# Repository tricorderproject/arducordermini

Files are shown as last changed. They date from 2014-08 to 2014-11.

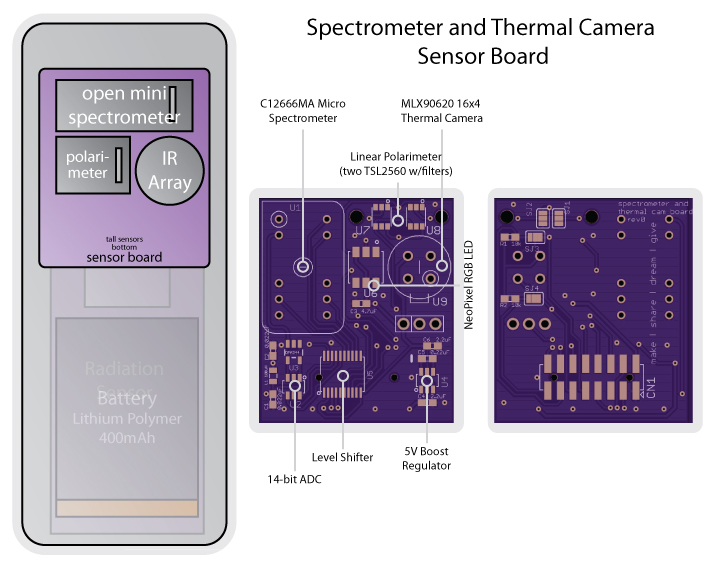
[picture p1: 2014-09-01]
hardware/pictures/spectrometer_rev0_layout.jpg

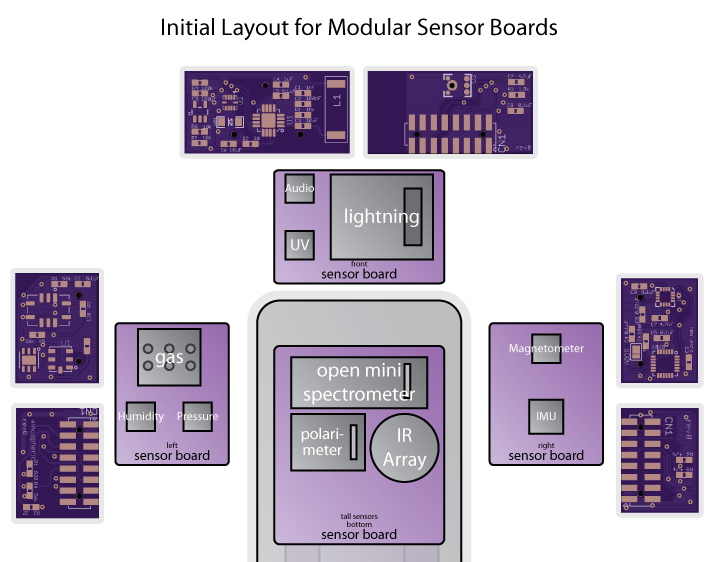
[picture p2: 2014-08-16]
hardware/pictures/sensorboards_rev0_layout.jpg

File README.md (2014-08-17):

Arducorder Mini
======

Arducorder Mini -- an Arduino-compatible Open Source Science Tricorder Project  
http://www.tricorderproject.org  
Copyright (C) 2014  Peter Jansen and the Tricorder project  
peter@tricorderproject.org  

*This is a work in progress*

# Introduction

This is the third iteration of the Open Source Science Tricorder prototypes, a series of science tricorder-like devices.  

Unlike the first two prototypes, this version has been designed from the ground up to be easy to manufacture, and to foster a community of open source developers and users.  The firmware is Arduino-compatible through the ChipKit MAX32 platform, and is being designed to provide advanced functionality for scientific use while being easy enough for beginners to meaningfully modify. 

# Concept
It is my deep belief that knowledge brings about positive change. 

We could live in a world where the same instrument that can show a child how much chlorophyll is in a leaf could also show how them much pollution is in the air around us, or given off by one's car. As an educator and a researcher, I feel that if people could easily discover things about their worlds that were also important social topics, that they would then make positive social choices, like reducing their emissions, or petitioning for cleaner industry in their communities. 

By having access to general inexpensive sensing tools, people can learn about healthy leaves, clean air, clouds and the water cycle, energy efficient homes — and visualize abstract concepts like spectra or magnetism. 

As a tool for exploration, we can discover things around us that we don't already know. And that's what it's about. Little discoveries, everywhere.

# Open Source

This project is open hardware and is released under various open licenses.  Please see LICENSES.TXT for details.

# Warning

**DISCLAIMER OF WARRANTIES AND LIMITATION OF LIABILITY.**

UNLESS OTHERWISE SEPARATELY UNDERTAKEN BY THE LICENSOR, TO THE EXTENT POSSIBLE, THE LICENSOR OFFERS THE LICENSED MATERIAL AS-IS AND AS-AVAILABLE, AND MAKES NO REPRESENTATIONS OR WARRANTIES OF ANY KIND CONCERNING THE LICENSED MATERIAL, WHETHER EXPRESS, IMPLIED, STATUTORY, OR OTHER. THIS INCLUDES, WITHOUT LIMITATION, WARRANTIES OF TITLE, MERCHANTABILITY, FITNESS FOR A PARTICULAR PURPOSE, NON-INFRINGEMENT, ABSENCE OF LATENT OR OTHER DEFECTS, ACCURACY, OR THE PRESENCE OR ABSENCE OF ERRORS, WHETHER OR NOT KNOWN OR DISCOVERABLE. WHERE DISCLAIMERS OF WARRANTIES ARE NOT ALLOWED IN FULL OR IN PART, THIS DISCLAIMER MAY NOT APPLY TO YOU.

TO THE EXTENT POSSIBLE, IN NO EVENT WILL THE LICENSOR BE LIABLE TO YOU ON ANY LEGAL THEORY (INCLUDING, WITHOUT LIMITATION, NEGLIGENCE) OR OTHERWISE FOR ANY DIRECT, SPECIAL, INDIRECT, INCIDENTAL, CONSEQUENTIAL, PUNITIVE, EXEMPLARY, OR OTHER LOSSES, COSTS, EXPENSES, OR DAMAGES ARISING OUT OF THIS PUBLIC LICENSE OR USE OF THE LICENSED MATERIAL, EVEN IF THE LICENSOR HAS BEEN ADVISED OF THE POSSIBILITY OF SUCH LOSSES, COSTS, EXPENSES, OR DAMAGES. WHERE A LIMITATION OF LIABILITY IS NOT ALLOWED IN FULL OR IN PART, THIS LIMITATION MAY NOT APPLY TO YOU.

THE DISCLAIMER OF WARRANTIES AND LIMITATION OF LIABILITY PROVIDED ABOVE SHALL BE INTERPRETED IN A MANNER THAT, TO THE EXTENT POSSIBLE, MOST CLOSELY APPROXIMATES AN ABSOLUTE DISCLAIMER AND WAIVER OF ALL LIABILITY.

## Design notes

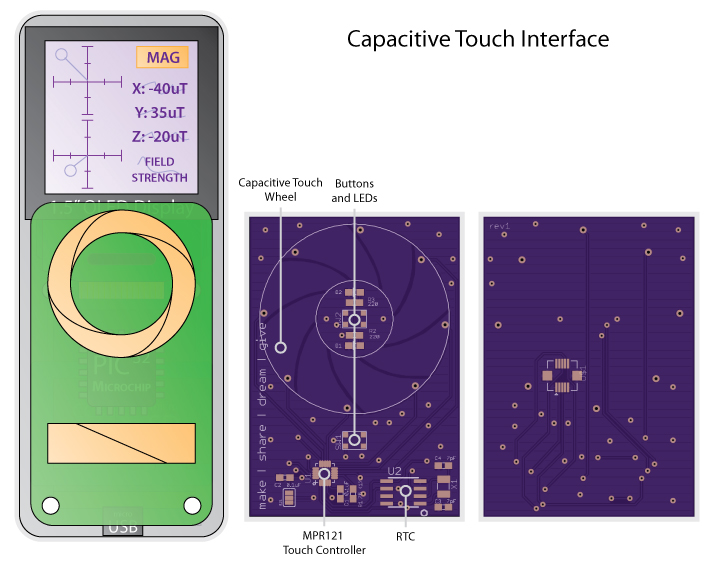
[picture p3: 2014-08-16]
hardware/pictures/touch_rev1_layout.jpg

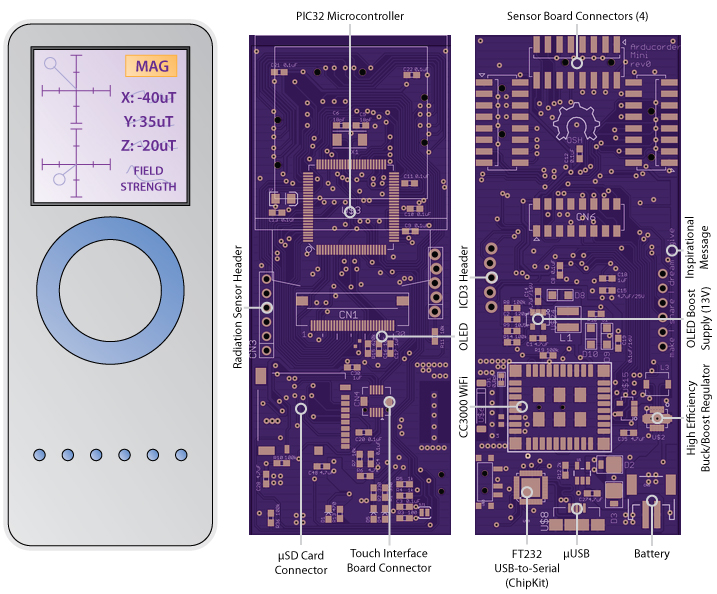
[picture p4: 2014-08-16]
hardware/pictures/motherboard_rev0_layout.jpg

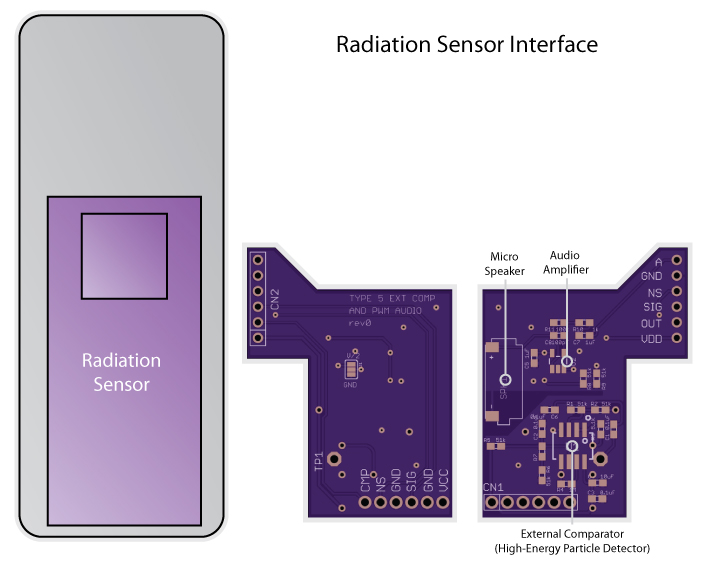
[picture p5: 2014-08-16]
hardware/pictures/radiation_rev0_layout.jpg

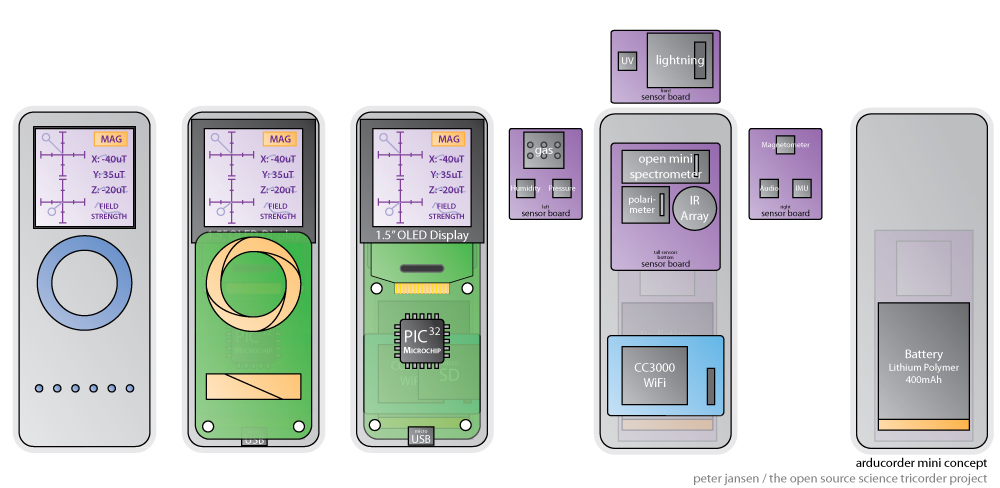
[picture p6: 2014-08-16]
concept/conceptualdrawing_landscape1.jpg

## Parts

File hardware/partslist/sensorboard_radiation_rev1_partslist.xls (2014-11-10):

Arducorder Mini Radiation Sensor Interface Board rev1 partslist (Oct 27/2014)
Part | Value | Part Number | Package | Function | Source | Website | Notes
NOTE: Recommended minimum 16V on all capacitors, when possible.
NOTE: Recommended minimum 1% on all resistors – this is especially important on the radiation sensor board.
C1 | 0.1uF | CAP0603 | 603
C2 | 0.1uF | CAP0603 | 603
C3 | 0.1uF | CAP0603 | 603
C4 | 10uF | CAP0603 | 603
C5 | 1uF | CAP0603 | 603
C6 | 0.1uF | CAP0603 | 603
C7 | 1uF | CAP0603 | 603
C8 | 100pF | CAP0603 | 603
CN1 | 1x06 | e.g. PBC06SAAN | 0.1” header | Header between board and Type 5 connector |  |  | Standard breakaway – many substititons possible.
CN2 |  | PHT-106-01-L-S |  | Motherboard connector | Samtec | http://www.samtec.com/ | Can be substituted for another 0.1” pitch connector. This one has to be ordered from Samtec, but appears very mechanically stable.
R1 | 51k |  | 603
R2 | 51k |  | 603
R3 | 5.1K |  | 603
R4 | 1M |  | 603
R5 | 51k |  | 603
R6 | 51k |  | 603
R7 | 2.7k/1% minimum |  | 603 | Radiation Sensitivity Calibration Resistor
R8 | 51k |  | 603
R9 | 51k |  | 603
R10 | 1k |  | 603
R11 | 1M |  | 603
R12 | 10k |  | 603
R13 | 10k |  | 603
R14 | 10k |  | 603
SPK1 |  | 2403 260 00106 (KNOWLES) |  | Mini speaker | Digikey |  | Digikey #: 423-1208-1-ND
U1 |  | AD8607 | SO8 | Radiation amplifier/comparator | Digikey
U2 |  | OPA344NA/250 | SOT23-5 | Speaker amplifier | Digikey
RAD1 |  | Radiation Watch Type 5 |  | Radiation sensor | RadiationWatch | http://www.radiation-watch.org/

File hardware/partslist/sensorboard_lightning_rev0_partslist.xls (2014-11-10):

Arducorder Mini Lightning/UV Sensor Board rev0 partslist (Oct 27/2014)
Part | Value | Part Number | Package | Function | Source | Website | Notes
NOTE: Recommended minimum 16V on all capacitors, when possible.
NOTE: Recommended minimum 1% on all resistors
C1 | 1nF |  | 603
C2 | 100pF |  | 603
C3 | 10uF |  | 603
C4 | 1uF |  | 603
C5 | 0.1uF |  | 603
C6 | 10uF |  | 603
C7 | 4.7uF |  | 603
C8 | 100pF |  | 603
C9 | 0.1uF |  | 603
CN1 |  | 0877591650 (MOLEX) |  | Sensor board connector | Digikey
L1 | 100uH | MA5532 |  | Lightning Antenna | Digikey
LED1 |  |  | 1206 | DNP |  |  | Optional LED for experimenting with the distance measurement function of the Si1145. It's very short range, but the LED footprint is included if you'd like to.
R1 | 10k |  | 603
R2 | 30 |  | 603
R3 | 1.5k |  | 603
R4 | 100k |  | 603
R5 | 10k |  | 603
R6 | 10k |  | 603
U1 |  | AS3935 | 16LD_MLPQ-(4X4MM) | Lightning sensor | Digikey
U2 |  | SI1145 |  | UV Sensor | Digikey
U3 |  | ADMP401 |  | Microphone | Digikey
U4 |  | OPA344NA/250 | SOT23-5 | Microphone amplifier | Digikey

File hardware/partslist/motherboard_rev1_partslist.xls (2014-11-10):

Arducorder Mini Motherboard rev1 partslist (Oct 27/2014)
Part | Value | Part Number | Package | Function | Source | Website | Notes
NOTE: Recommended minimum 16V on all capacitors, when possible.
C1 | 4.7uF |  | 603
C2 | 120pF/16V |  | 603
C3 | 0.1uF |  | 603
C4 | 0.1uF |  | 603
C5 | 18pF |  | 603
C6 | 18pF |  | 603
C8 | 0.1uF |  | 603
C9 | 0.1uF |  | 603
C10 | 0.1uF |  | 603
C11 | 0.1uF |  | 603
C12 | 0.1uF |  | 603
C13 | 0.1uF |  | 603
C14 | 4.7uF/16V |  | 603
C15 | 4.7uF/25V |  | 603
C16 | 1uF |  | 603
C17 | 1uF |  | 603
C18 | 1uF |  | 603
C19 | 0.1uF/16V |  | 603
C20 | 0.1uF |  | 603
C21 | 0.1uF |  | 603
C22 | 0.1uF |  | 603
C27 | 4.7uF |  | 603
C28 | 4.7uF |  | 603
C30 | 1uF |  | 603
C35 | 4.7uF |  | 603
C48 | 4.7uF |  | 603
C31 | 0.8pF |  | 402 | WiFi RF | Digikey
C7 | 10uF |  | EIA3216
CN1 |  | XF2M-3015-1A |  | OLED connector | Digikey
CN2 | 1X05 | 1X05 | 1X05 | DNP – ICD3 programming header | N/A
CN3 | FEMALE | PHF-106-01-L-S | 1X06 | Radiation board connector | Samtec | http://www.samtec.com/ | Can be substituted for another 0.1” pitch connector. This one has to be ordered from Samtec, but appears very mechanically stable.
CN4 | FEMALE | DF12B(3.0)-10DP-0.5V(86) |  | Touch board connector | Digikey
CN5 |  | PRT-08612 | SparkFun-Connectors | Battery connector | Sparkfun | https://www.sparkfun.com/products/8612
CN6 |  | 0791091007 (MOLEX) |  | Sensor board connector | Digikey
CN7 |  | 87368-1624 (MOLEX) |  | Sensor board connector | Digikey
CN8 |  | 87368-1624 (MOLEX) |  | Sensor board connector | Digikey
CN9 |  | 87368-1624 (MOLEX) |  | Sensor board connector | Digikey
D1 | Red | APT1608SRCPRV | 0603-LED | Charge LED | Digikey
D4 | Green | APT1608CGCK | 0603-LED | USB LED | Digikey
D5 | Blue | APT1608QBC/D | 0603-LED | USB LED | Digikey
D8 |  | PMEG2010AEH | SOD123F |  | Digikey
D9 |  | PMEG2010AEH | SOD123F |  | Digikey
D10 |  | PMEG2010AEH | SOD123F |  | Digikey
D2 |  | UPS115UE3/TR7 | DO-214BA |  | Digikey
D3 |  | UPS115UE3/TR7 | DO-214BA |  | Digikey
L1 | NR4018T100M | INDUCTORNR4018T100M | NR4018T100M |  | Digikey
L3 | 2.2uH | VLF4012AT-2R2M1R5 | VLF4012A |  | Digikey
L6 | 3.3nH |  | 402 | WiFI RF | Digikey
NOTE: Recommended minimum 1% on all resistors
R1 | 330 |  | 603
R2 | 330 |  | 603
R3 | 100 |  | 603
R4 | 1k |  | 603
R5 | 1k |  | 603
R6 | 4.7k |  | 603
R7 | 10k |  | 603
R8 | 100k |  | 603
R9 | 10.5k |  | 603
R10 | 100k |  | 603
R11 | 10k |  | 603
R12 | 2k |  | 603
R13 | 470 |  | 603
R14 | 100k |  | 603
R15 | 620k |  | 603
R16 | 4.7k |  | 603
R17 | 4.7k |  | 603
R18 | 51 |  | 603
R19 | 100k |  | 603
R36 | 100k |  | 603
U2 |  | TPS63001 |  | 3.3V buck/boost DC-DC converter | Digikey
U3 |  | PIC32MX795F512L-80I/PF | SQFP-S-14X14-100 | Microcontroller | Digikey
U5 |  | KPS-1290 |  | Power switch | See notes |  | Common footprint – substitute PCM12SMTR or MA12RTR, available at Digikey
U6 |  | 2500AT44M0400E |  | Wifi Antenna | Digikey
U7 |  | DM3B (HIROSE) |  | Micro SD Card socket | Digikey
U8 |  | FCI-10104110-0001LF |  | Micro USB connector | Digikey
U9 |  | FT232RQ | QFN-32 | USB to serial bridge | Digikey
U12 |  | CC3000MODR |  | Wifi module | Digikey
U15 |  | NL17SZ125DTT1G | TSOP-5 | Buffer | Digikey
U24 |  | FAN5331SX | TSOP-5 | OLED 13V booster | Digikey
U1 |  | MCP73831 | SOT23-5 | LiPoly charge controller | Digikey
X1 | 8.000MHz | ABM7-8.000MHZ-D-2-Y-T | CYRSTAL-6.0X3.5MM |  | Digikey
OLED1 |  | UG-2828GDEDF11 |  | 1.5” OLED | BuyDisplay | http://www.buydisplay.com/default/serial-spi-1-5-inch-color-oled-display-128x128-graphic-module-ssd1351 | Seems to have many part numbers. Also ER-OLED015
BAT1 | 500mAh | 1578 |  | LiPoly battery | Adafruit | http://www.adafruit.com/products/1578

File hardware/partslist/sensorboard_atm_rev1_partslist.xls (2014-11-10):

Arducorder Mini Atmospheric Sensor Board rev1 partslist (Oct 27/2014)
Part | Value | Part Number | Package | Function | Source | Website | Notes
NOTE: Recommended minimum 16V on all capacitors, when possible.
NOTE: Recommended minimum 1% on all resistors
C1 | 0.1uF |  | 603
C2 | 0.1uF |  | 603
CN1 |  | 0877591650 (MOLEX) |  | Sensor board connector | Digikey
R1 | 541 |  | 603
R2 | 18 |  | 603
R3 | 86 |  | 603
R4 | 56k |  | 603
R5 | 56k |  | 603
R6 | 56k |  | 603
R7 | 1k |  | 603
R8 | 1k |  | 603
R9 | 1k |  | 603
R10 | 100k |  | 603
R11 | 100k |  | 603
R12 | 100k |  | 603
U1 |  | BMP180 |  | Pressure sensor | Digikey
U2 |  | HTU21D |  | Humidity sensor | Digikey
U3 |  | MICS-6814 |  | Gas sensor | CDI
U4 |  | IRLML6401 | SOT23-3L |  | Digikey
U5 |  | IRLML6401 | SOT23-3L |  | Digikey
U6 |  | IRLML6401 | SOT23-3L |  | Digikey

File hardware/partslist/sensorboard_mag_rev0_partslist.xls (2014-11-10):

Arducorder Mini Magnetometer Sensor Board rev0 partslist (Oct 27/2014)
Part | Value | Part Number | Package | Function | Source | Website | Notes
NOTE: Recommended minimum 16V on all capacitors, when possible.
NOTE: Recommended minimum 1% on all resistors
C3 | 2.2nF/50V |  | 603
C4 | 0.1uF |  | 603
C5 | 0.1uF |  | 603
C6 | 10nF |  | 603
C7 | 4.7uF |  | 603
C8 | 0.22uF |  | 603
C9 | 0.1uF |  | 603
CN1 |  | 0877591650 (MOLEX) |  | Sensor board connector | Digikey
R5 | 4.7k |  | 603
R6 | 4.7k |  | 603
U2 |  | HMC5883L | 16LPCC | Magnetometer | Digikey
U10 |  | MPU-9150 | LGA-24-(4X4MM) | Inertial measurement unit | Digikey

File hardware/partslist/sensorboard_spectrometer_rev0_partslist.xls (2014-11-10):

Arducorder Mini Spectrometer/Thermal Board rev0 partslist (Oct 27/2014)
Part | Value | Part Number | Package | Function | Source | Website | Notes
NOTE: Recommended minimum 16V on all capacitors, when possible.
NOTE: Recommended minimum 1% on all resistors
C1 | 0.022uF |  | 603
C2 | 0.022uF |  | 603
C3 | 4.7uF |  | 603
C4 | 2.2uF |  | 603
C5 | 0.22uF |  | 603
C6 | 2.2uF |  | 603
CN1 |  | 0877591650 (MOLEX) |  | Sensor board connector | Digikey
CN2 |  |  |  | DNP |  |  | Header/connector for optional light source for spectrometer
L1 | 100uH |  | 805 |  |  |  | Recommended: GLFR1608T101M-LR (TDK) or similar
R1 | 10k |  | 603 | DNP
R2 | 10k |  | 603 | DNP
U1 |  | C12666MA |  | Spectrometer | Hamamatsu
U2 |  | AD7940BRJZ | SOT-23-6L | 14-bit ADC | Digikey
U3 |  | OPA344NA/250 | SOT23-5 | Speaker amplifier | Digikey
U4 |  | REG710NA-5/250 | SOT-23-6L | 5V DC-DC boost converter | Digikey
U5 |  | TXS0108EPWR | TSSOP-20 | Level translator | Digikey
U6 |  | WS2812_NEOPIXEL | WS2812 | Light source | Adafruit
U7 |  | TSL2561T | TMB-6 | Light sensor | Digikey
U8 |  | TSL2561T | TMB-6 | Light sensor | Digikey
U9 |  | MLX90620 | MLX90620 | Thermal camera sensor | Digikey

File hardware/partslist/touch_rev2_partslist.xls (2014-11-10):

Arducorder Mini Capacitive Touch Wheel Board rev2 partslist (Oct 27/2014)
Part | Value | Part Number | Package | Function | Source | Website | Notes
NOTE: Recommended minimum 16V on all capacitors, when possible.
NOTE: Recommended minimum 1% on all resistors
C1 | 0.1uF |  | 603
C2 | 0.1uF |  | 603
C3 | 7pF |  | 603
C4 | 7pF |  | 603
D1 |  |  | 0603-LED | DNP |  |  | LEDs for glowing OK button are optional and currently untested
D2 |  |  | 0603-LED | DNP
R1 | 75k/1% |  | 603 | Touch calibration resistor
R2 | 220 |  | 603 | DNP
R3 | 220 |  | 603 | DNP
SW1 |  | KMT071 |  | Tactile button | Digikey
SW2 |  | KMT071 |  | Tactile button | Digikey
U$1 |  | DF12B(3.0)-10DS-0.5V(86) |  | Motherboard connector | Digikey
U1 |  | MPR121QR2 | QFN-3X3-20 | Touch controller | Digikey
U2 |  | M41T82ZM6F | 8-SOIC | Real time clock | Digikey
X1 | 32.768kHz | 9HT10 |  | Real time clock crystal | Digikey

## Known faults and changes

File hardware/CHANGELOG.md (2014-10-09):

Change Log
======

**Motherboard**  
*rev1* (Oct 2014)
- Corrected two sets of switched power pins on the PIC32 (15/16, and 62/65)
- Added missing 4.7k pull-up resistors (R17, R18) for SDA1/SCL1.  These were previously added to the Magnetic Field Sensor r0 board as optional in the interim.  
- ERRATA NOTE: The FT232 lights appear to be on when the USB is connected, but the device (3.3V main bus) is off.  This should leave VCCIO at 0V, which might lead to unpredictable behaviour, or might be plain out of specifications. RESPONSE: Options are to power the FT232 internally, with VCCIO at its 3.3V output, which should pull-up UART lines, and may provide unintended partial power to PIC32.  This might lead to unpredictable boot-up behaviour of the PIC32, so we'll leave this as-is for now. 
- Radiation sensor connector (CN3) part number identified as Samtec PHF-106-01-L-S.  Drills on connector increased to 1.2mm to accommodate. 
- Capacitive touch sensor (CN4) has alignment holes, and there is no low-profile (<3mm) yet mechanically stable connector option that I'm aware of.  Added four 2mm mount points at the four corners of the capacitive touch board, intended for 4x M2 machine screws, and 4x nylon stand-offs (3mm height). 
- Board sized increased slightly -- 4mm in width and 4mm in width.  This was required to accommodate the mount points. 
- ERRATA: A few pixels on the OLED occasionally stay on when the power switch is off.  Double check that the pull-down on the 13V boost enable line is functioning properly.  RESPONSE: After a fresh look, the architecture of the FAN5331 booster circuit appears to allow the VIN current to pass through when the booster is disabled.  This has the undesired effect of leaving 3-5V on the OLED voltage line when the device should be powered down, both drawing power and leaving a few stray pixels illuminated.  Changed the FAN5331 voltage input source from VIN to 3.3V, after the primary TPS63001 buck/boost regulator.  This lowers efficiency a bit, but means the FAN5331 booster will have no voltage source when the device is off, and will prevent power drain. 
- Moved capacitive touch board connector to a lower position, to facilitate the mount holes on the mating connector not intersecting with the capacitive touch wheel. 
- Increased and oversized power trace widths to OLED, and CC3000.  There weren't any previous issues with the CC3000, but the OLED would flicker if the display was full white, full intensity (~300ma).  

**Capacitive Touch Sensor board**  
*rev2*
- Designed to mate with motherboard rev1
- Added four M2 machine screw mount points to motherboard, for mechanical stability. 
- Moved all components to the bottom of the board, to facilitate mounting in a case.  (The two pushbuttons are the two exceptions)
- Capacitive touch wheel electrodes are wired to the MPR121 in a slightly different pattern -- the touch wheel calculations will likely be offset, or reversed. 
- Added slot at the bottom of the board for motherboard LEDs (charging, FT232) to shine through. 
- Added mount holes to connector, for increased mechanical stability. 

**Sensor Board: Radiation board (with mini speaker)**  
*rev1*
- Connector to motherboard (CN2) part number identified as Samtec PHT-106-01-L-S.  Drills on connector increased to 1.2mm to accommodate.
- R7 part number needs to be specified -- this can be tuned, but I believe around 9k.
- Precision pull-up resistors for output signals (OUT, SIG, NS) specified -- (R12 to R14). 10k pullups should give between a 30uS and 70uS pulse duration. 
- Speaker is quiet, and I'm not great with audio circuitry -- moved some of the opamp passives to the accessible side of the board so that they can be tinkered with, if required.

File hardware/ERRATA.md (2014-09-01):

Known Errata
======

**Motherboard**  
*rev0*
- Two sets of power pins on the PIC32 are switched (15/16, and 62/65)
- SDA1/SCL1 are missing 4.7k pull-up resistors on the motherboard.  These were added to the Magnetic Field Sensor r0 board as optional in the interum.
- The FT232 lights appear to be on when the USB is connected, but the device (3.3V main bus) is off.  This should leave VCCIO at 0V, which might lead to unpredictable behaviour, or might be plain out of specifications. 
- Radiation sensor connector (CN3) still needs a part number.  The holes may have to be increased slightly, and location may have to shift a little. 
- Capacitive touch sensor (CN4) likely needs a bit more mechanically steady mounting, perhaps a different connector near the bottom of the board/USB connector.  If the same connector is used, the pads for the mount point need to be extended out about 0.5mm . 
- A few pixels on the OLED occasionally stay on when the power switch is off.  Double check that the pull-down on the 13V boost enable line is functioning properly. 

**Capacitive Touch Sensor board**  
*rev0*
- R1 should be 75k (not 75 ohms)
- C1 should be Hirose DF12 series.  (I believe DF12(3.0)-10DS-0.5V(86) )

*rev1*
- The parts likely need to be moved to the bottom of the board to ease placing a dialectric overlay on top.
- The RTC should be moved to the motherboard, if possible. 
- Connector to motherboard (CN1) likely needs to be more mechanically stable to keep the board in place during touch events, perhaps by using a different connector near the bottom of the board/USB connector, or mount points to the case.  I believe the pads for the mount points on this connector have already been extended out 0.5mm, incase the same connector is reused. 

**Sensor Board: Magnetic Field/IMU board**  
*rev0*
- SJ1 I2C address solder jumper for the MPU9150 should be set to bridge 3.3V instead of GND by default, to set the MPU9150 address to 0x69 by default, and not conflict with the real time clock. 

**Sensor Board: Atmospheric Sensor board**  
*rev0*
- MiCS-6814 gas sensor needs 3 MOSFETs to drive the 3 heater lines, since the current will be more than the PIC32 lines can supply. 
- BMP180 sensor uncontacted, but I think the sensors I purchased from China during the BMP180 shortage may be counterfeit. 
- Analog and digital pins for the MiCS-6814 were swapped on the sensor board header

**Sensor Board: Lightning/UV/Sound board**  
*rev0*

**Sensor Board: Radiation board (with mini speaker)**  
*rev0*
- Connector to motherboard (CN1) still needs a part number.  The holes may have to be increased slightly, and location may have to shift a little. 
- R7 part number needs to be specified
- SJ1 VREF source for audio out needs to be determined (and SJ1 removed in the next revision) [NOTE: Both V/2 and GND references appear to work, but volume is low for both.  R11 may need to be adjusted upward (~1M), or this may be a property of the micro speaker]
- Precision pull-up resistors for output signals (OUT, SIG, NS)

**Sensor Board: Spectroscopy / Thermal Camera board**  
*rev0*

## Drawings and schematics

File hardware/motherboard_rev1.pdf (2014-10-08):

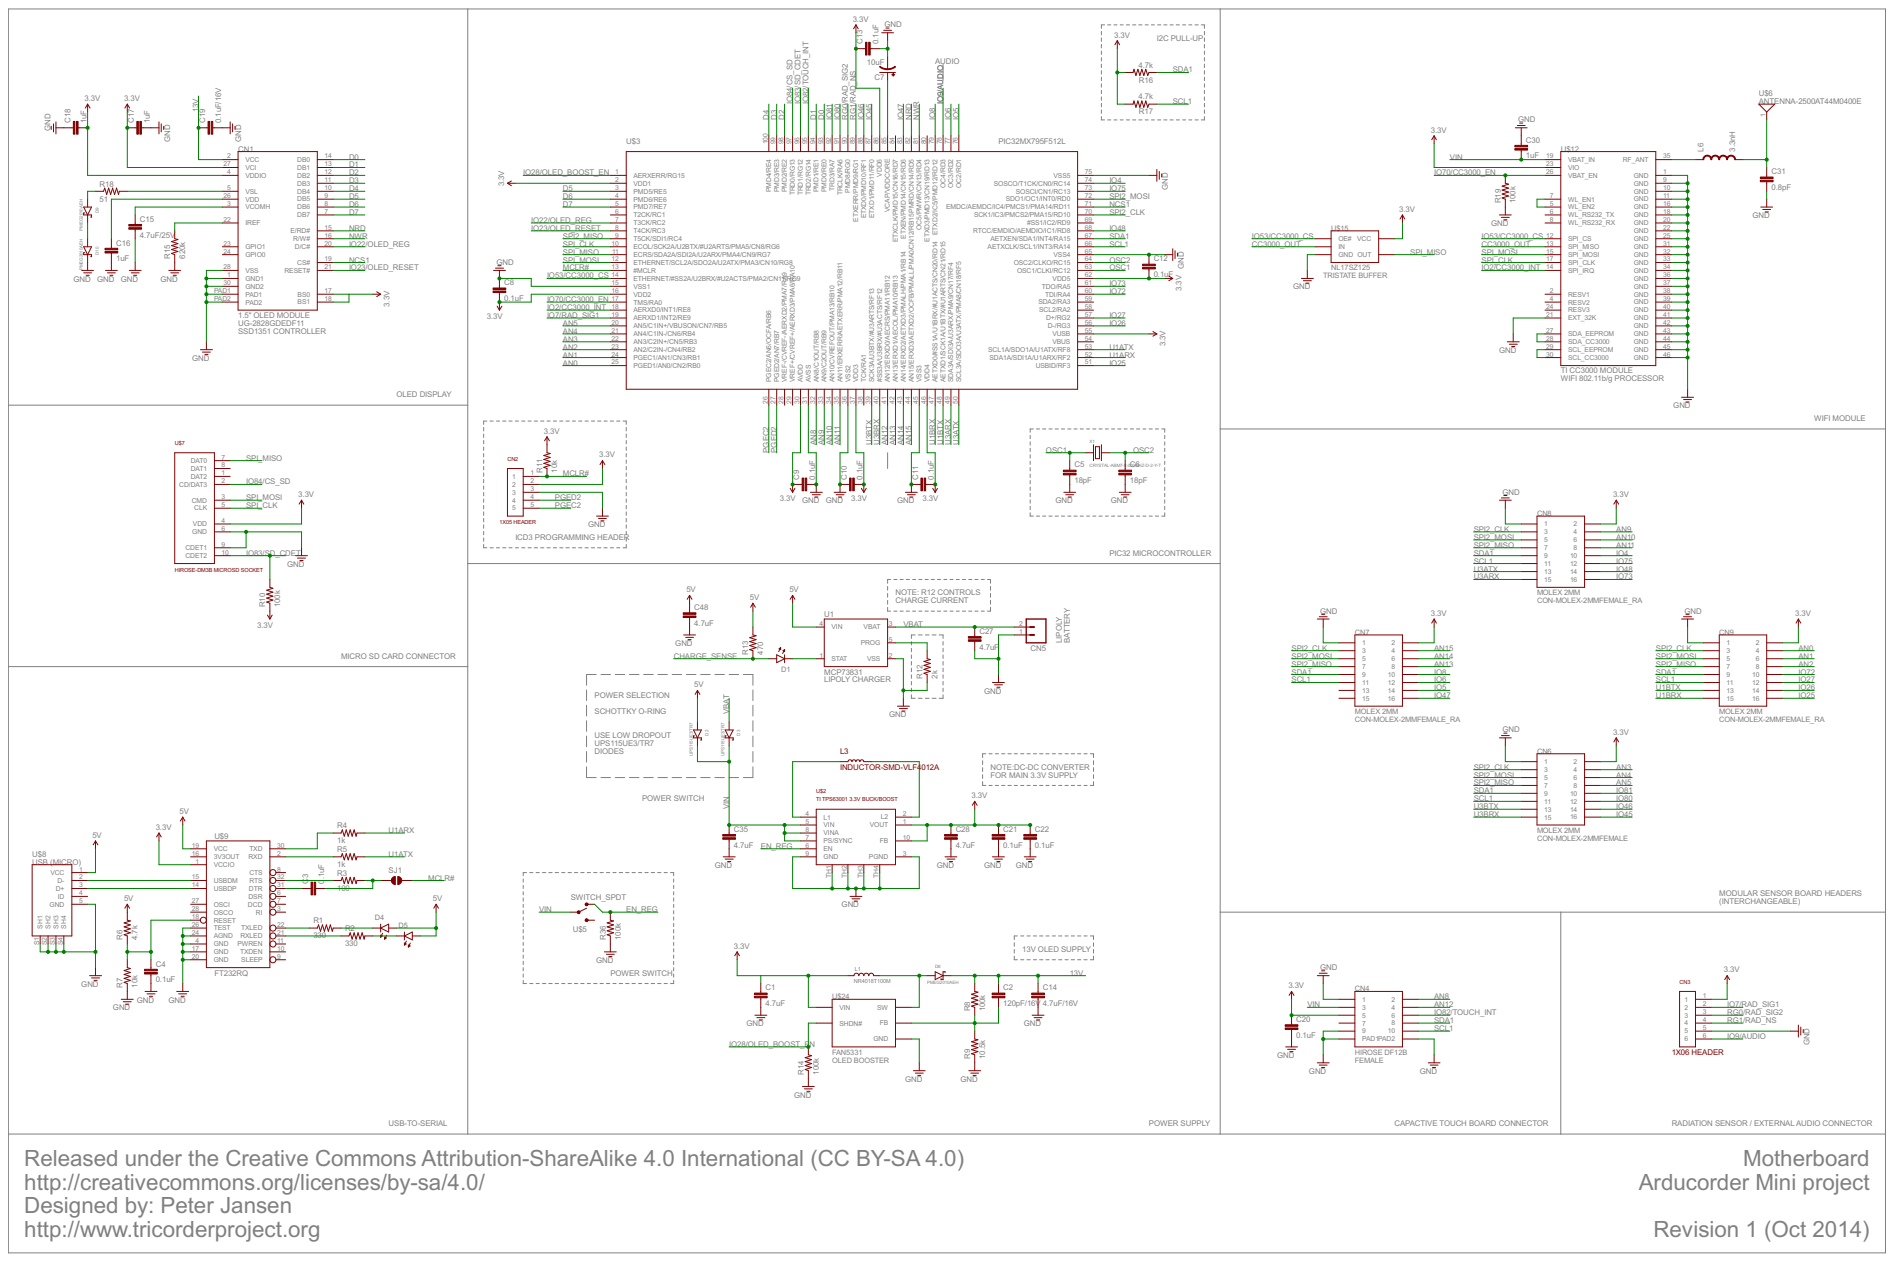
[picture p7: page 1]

1.5" OLED MODULE UG-2828GDEDF11 SSD1351 CONTROLLER

TI CC3000 MODULE WIFI 802.11b/g PROCESSOR

NOTE: R12 CONTROLS CHARGE CURRENT

MICRO SD CARD CONNECTOR

USE LOW DROPOUT UPS115UE3/TR7 DIODES

NOTE:DC-DC CONVERTER
FOR MAIN 3.3V SUPPLY

MODULAR SENSOR BOARD HEADERS
(INTERCHANGEABLE)

Released under the Creative Commons Attribution-ShareAlike 4.0 International (CC BY-SA 4.0)
http://creativecommons.org/licenses/by-sa/4.0/
Designed by: Peter Jansen

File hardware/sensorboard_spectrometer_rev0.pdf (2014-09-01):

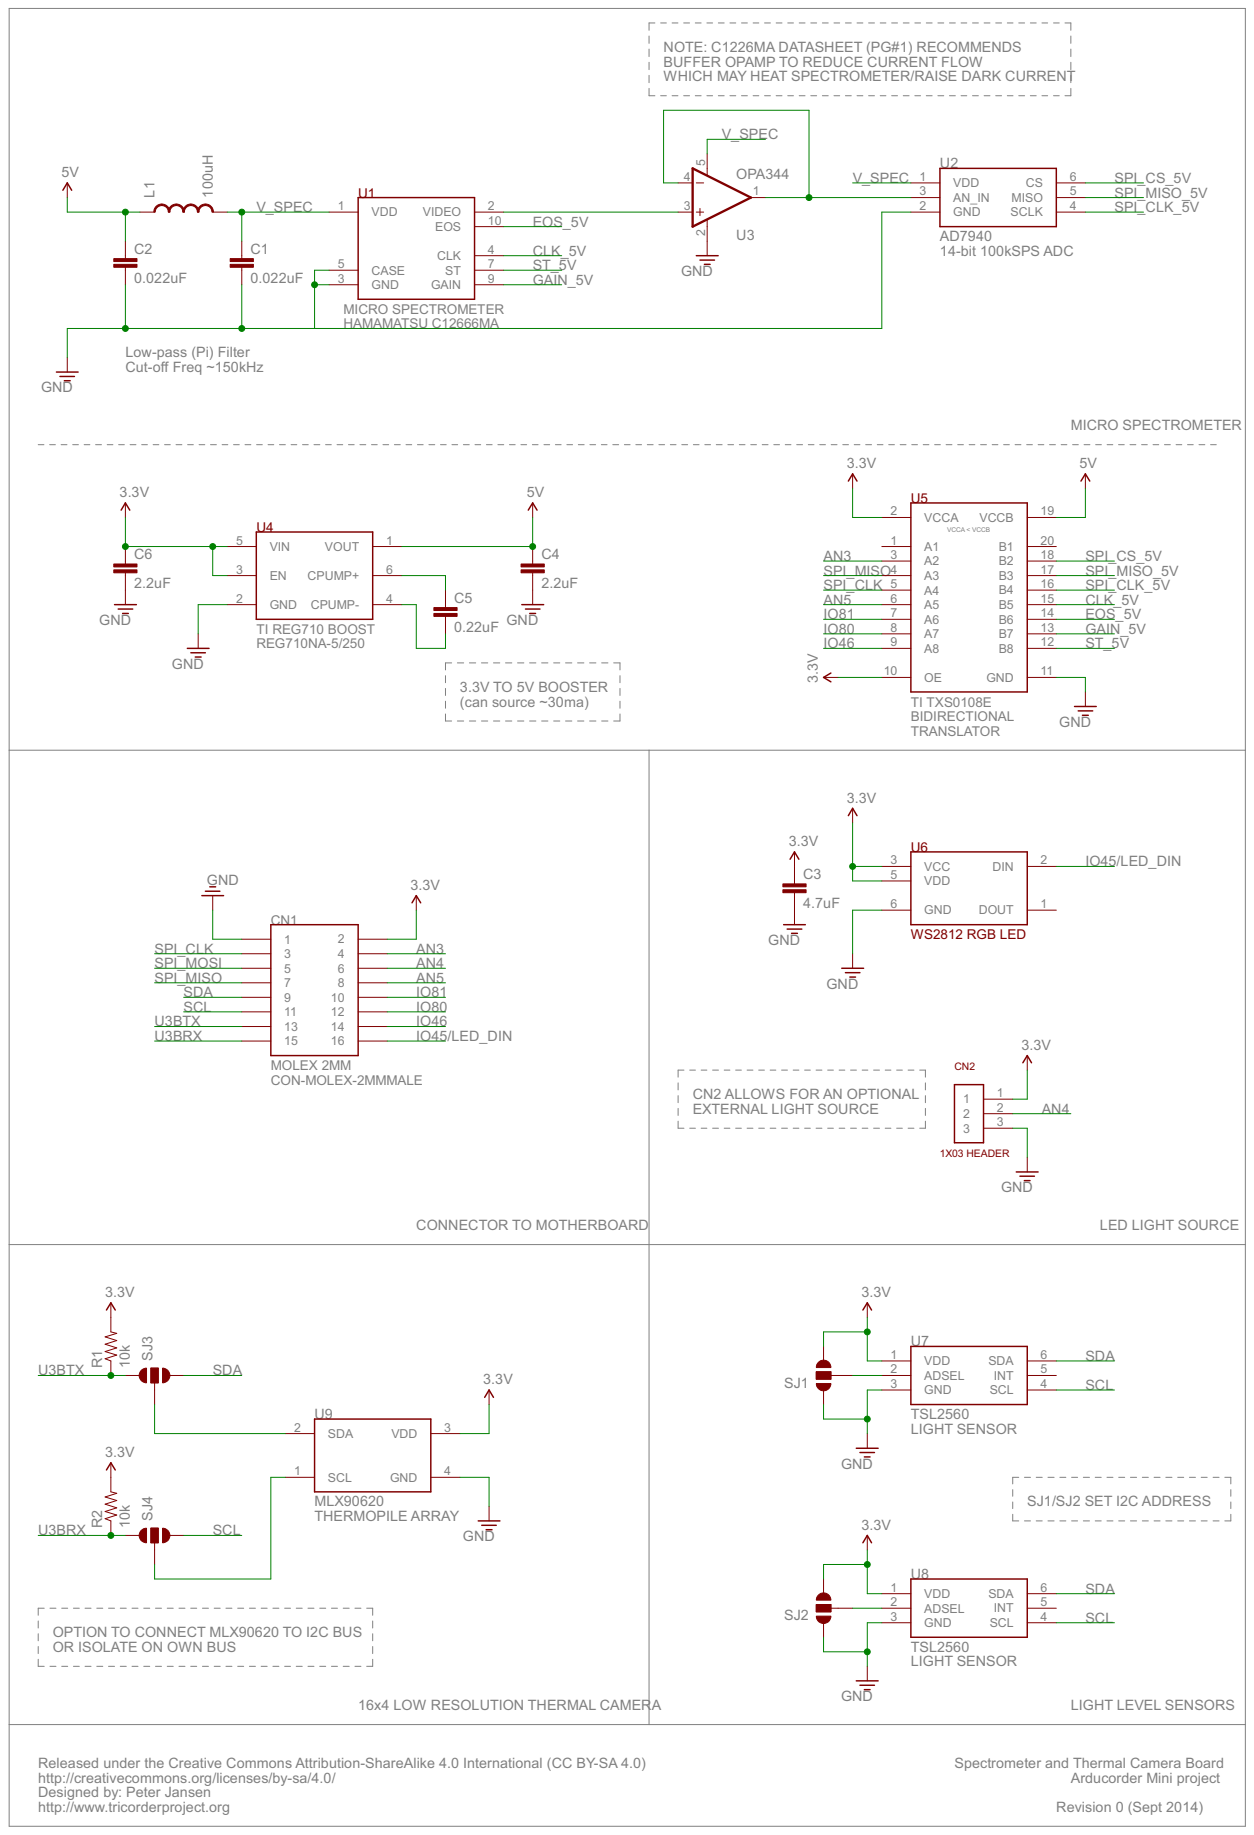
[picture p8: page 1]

NOTE: C1226MA DATASHEET (PG#1) RECOMMENDS
BUFFER OPAMP TO REDUCE CURRENT FLOW
WHICH MAY HEAT SPECTROMETER/RAISE DARK CURRENT

14-bit 100kSPS ADC MICRO SPECTROMETER

Low-pass (Pi) Filter Cut-off Freq ~150kHz

CN2 ALLOWS FOR AN OPTIONAL EXTERNAL LIGHT SOURCE

OPTION TO CONNECT MLX90620 TO I2C BUS OR ISOLATE ON OWN BUS

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

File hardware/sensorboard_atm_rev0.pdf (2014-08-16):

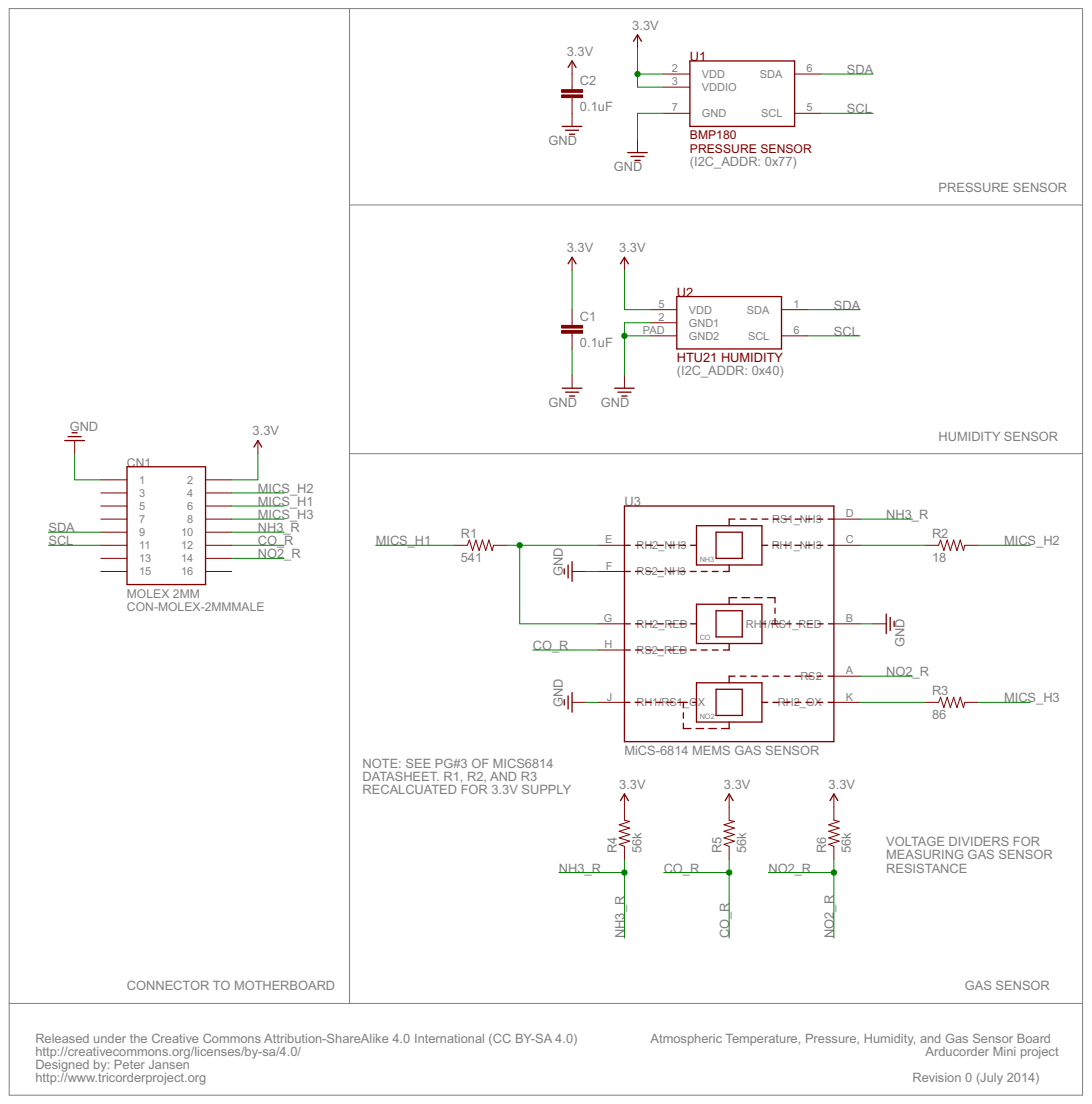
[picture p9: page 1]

NOTE: SEE PG#3 OF MICS6814
DATASHEET. R1, R2, AND R3
RECALCUATED FOR 3.3V SUPPLY

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

Atmospheric Temperature, Pressure, Humidity, and Gas Sensor Board

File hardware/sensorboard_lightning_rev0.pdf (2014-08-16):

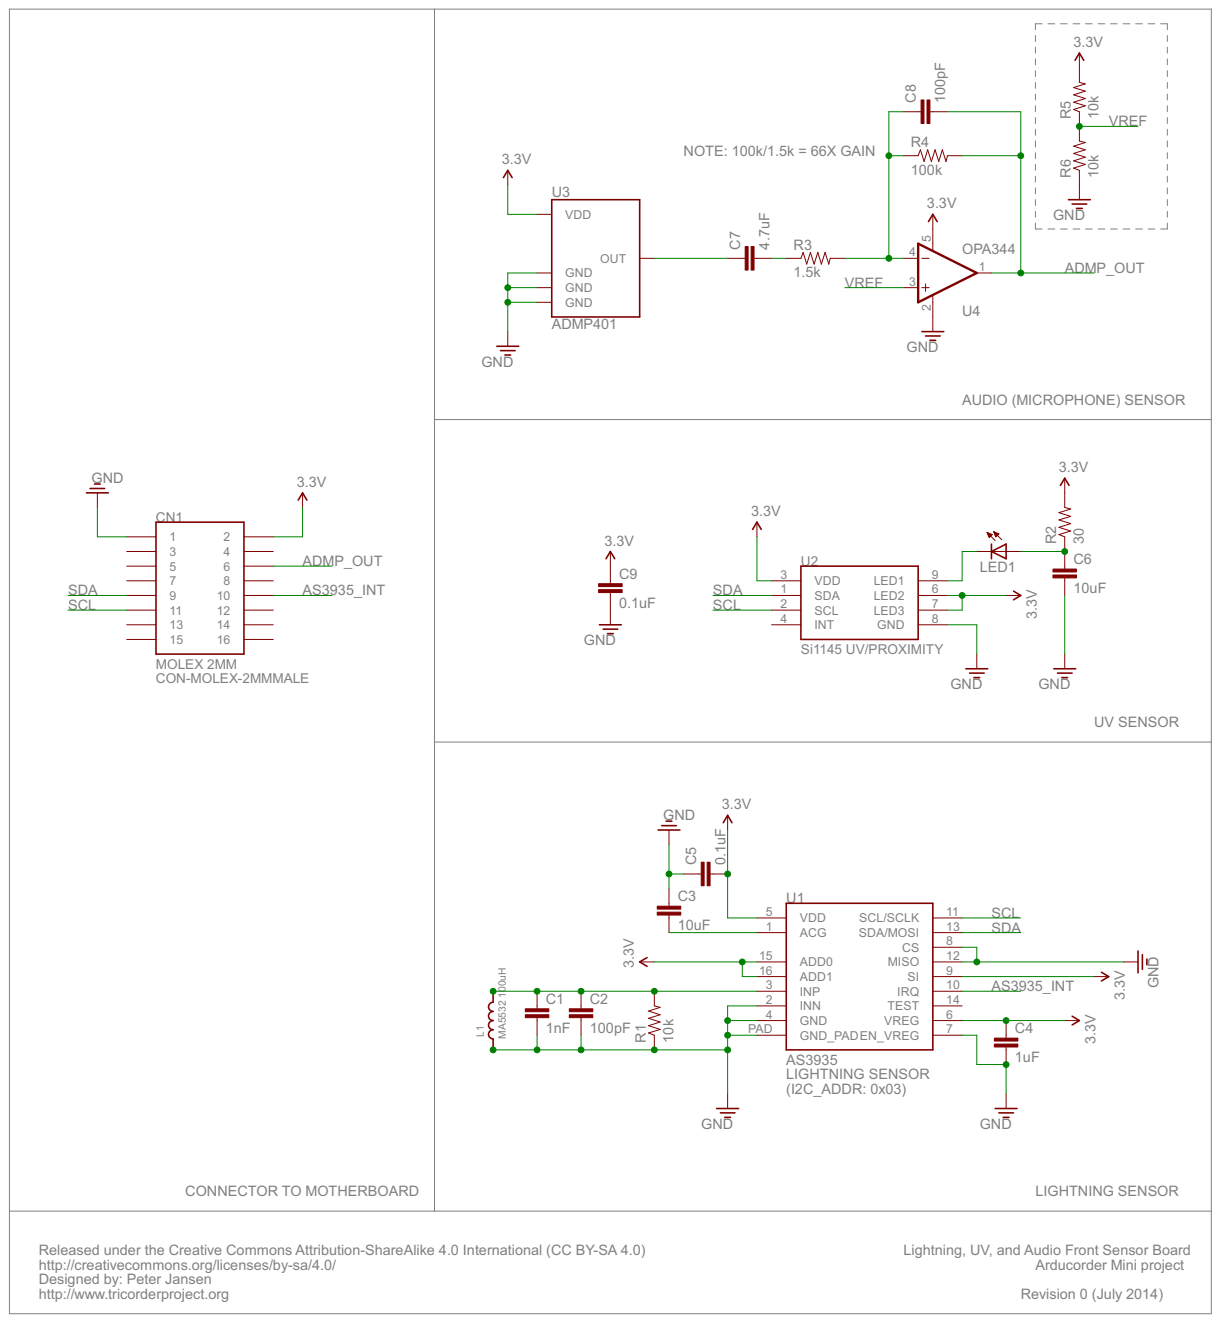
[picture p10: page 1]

U3VDD OUT GND GND GND

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

Lightning, UV, and Audio Front Sensor Board

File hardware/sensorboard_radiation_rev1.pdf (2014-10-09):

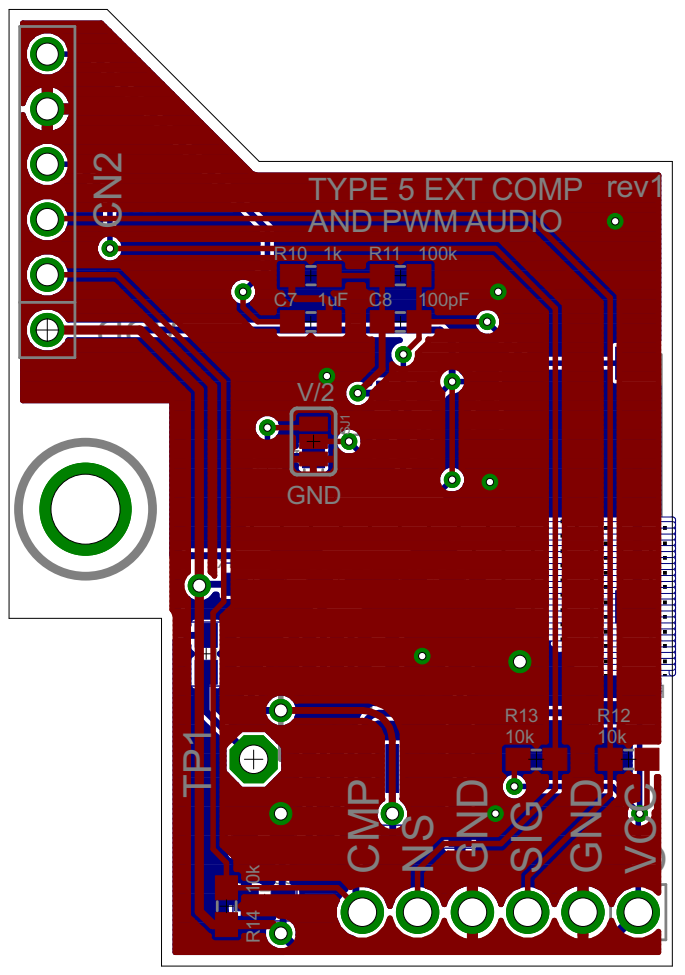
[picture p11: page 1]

GND

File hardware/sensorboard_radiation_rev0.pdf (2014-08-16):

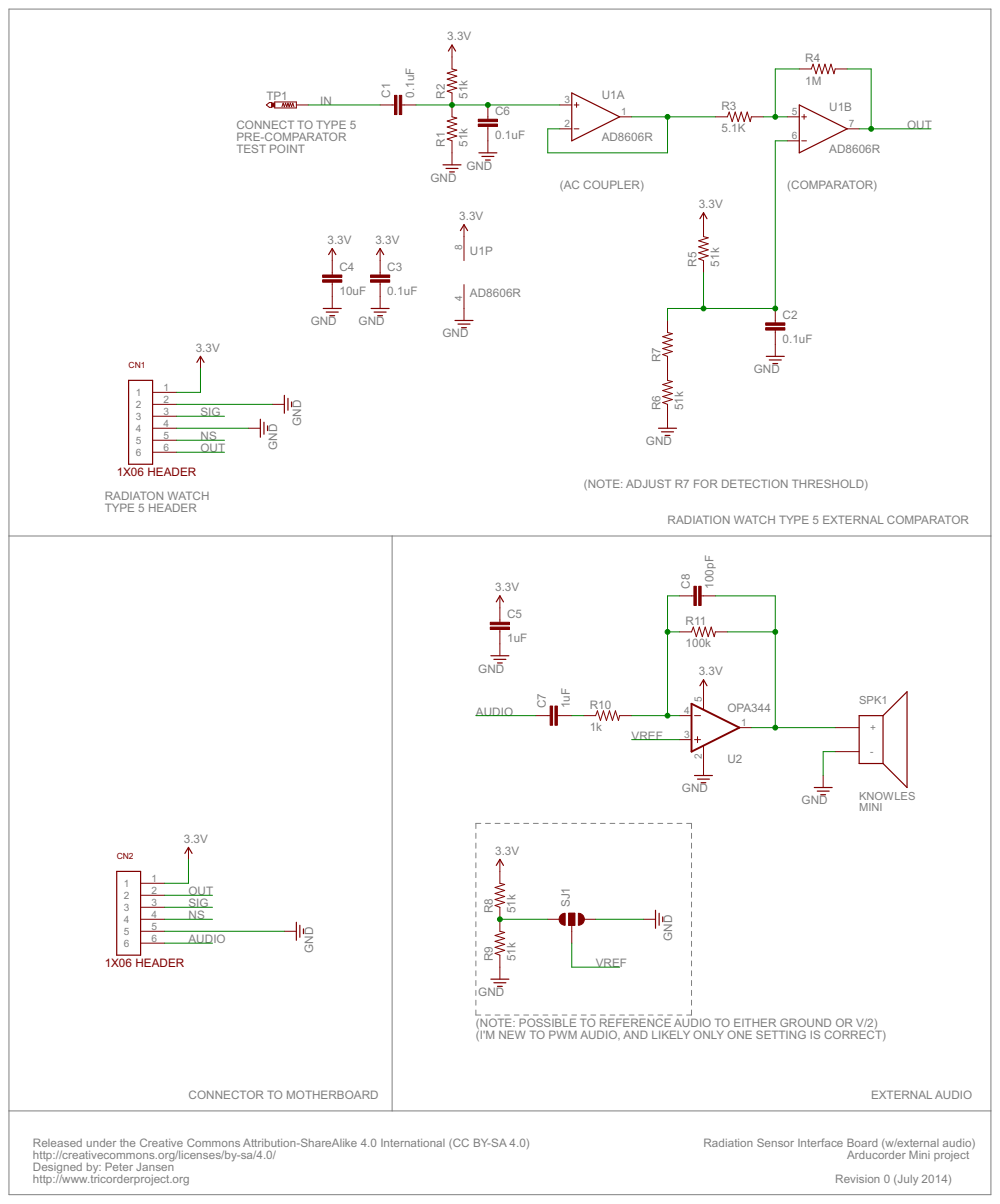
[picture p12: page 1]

(NOTE: ADJUST R7 FOR DETECTION THRESHOLD)

RADIATION WATCH TYPE 5 EXTERNAL COMPARATOR

(NOTE: POSSIBLE TO REFERENCE AUDIO TO EITHER GROUND OR V/2)

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

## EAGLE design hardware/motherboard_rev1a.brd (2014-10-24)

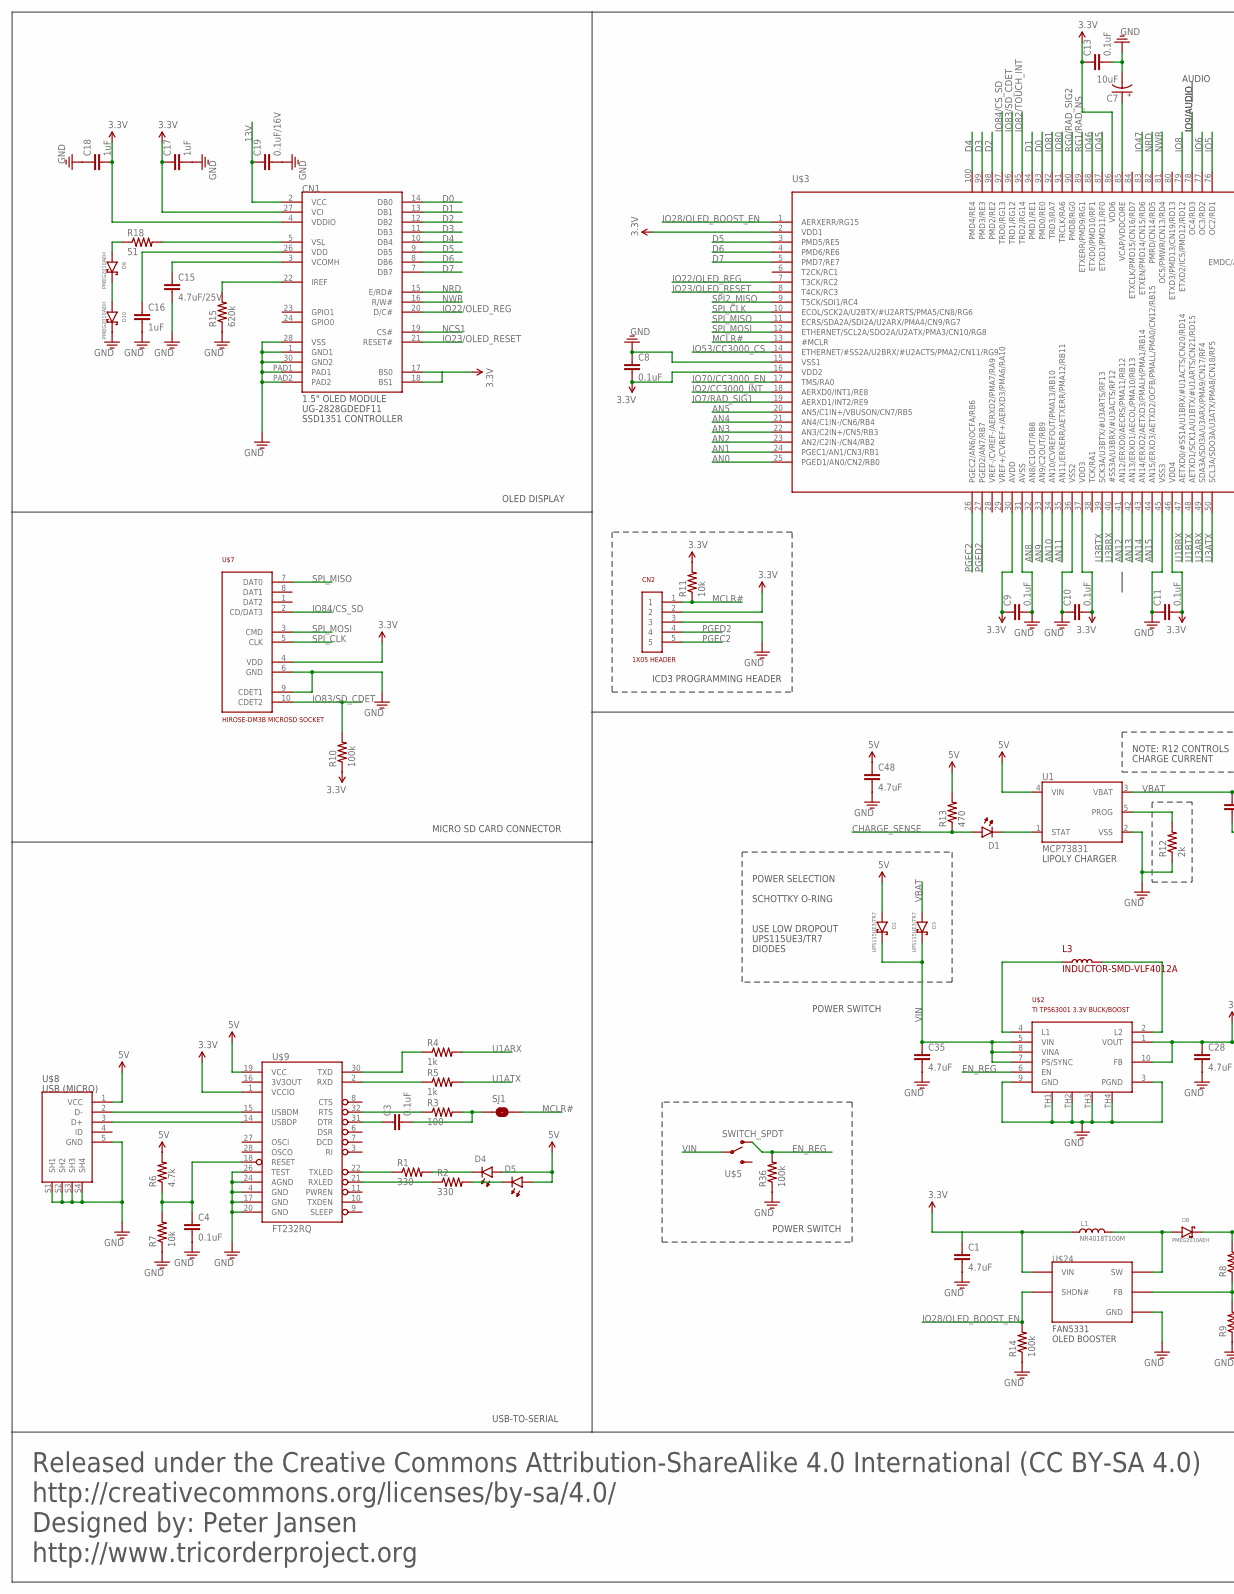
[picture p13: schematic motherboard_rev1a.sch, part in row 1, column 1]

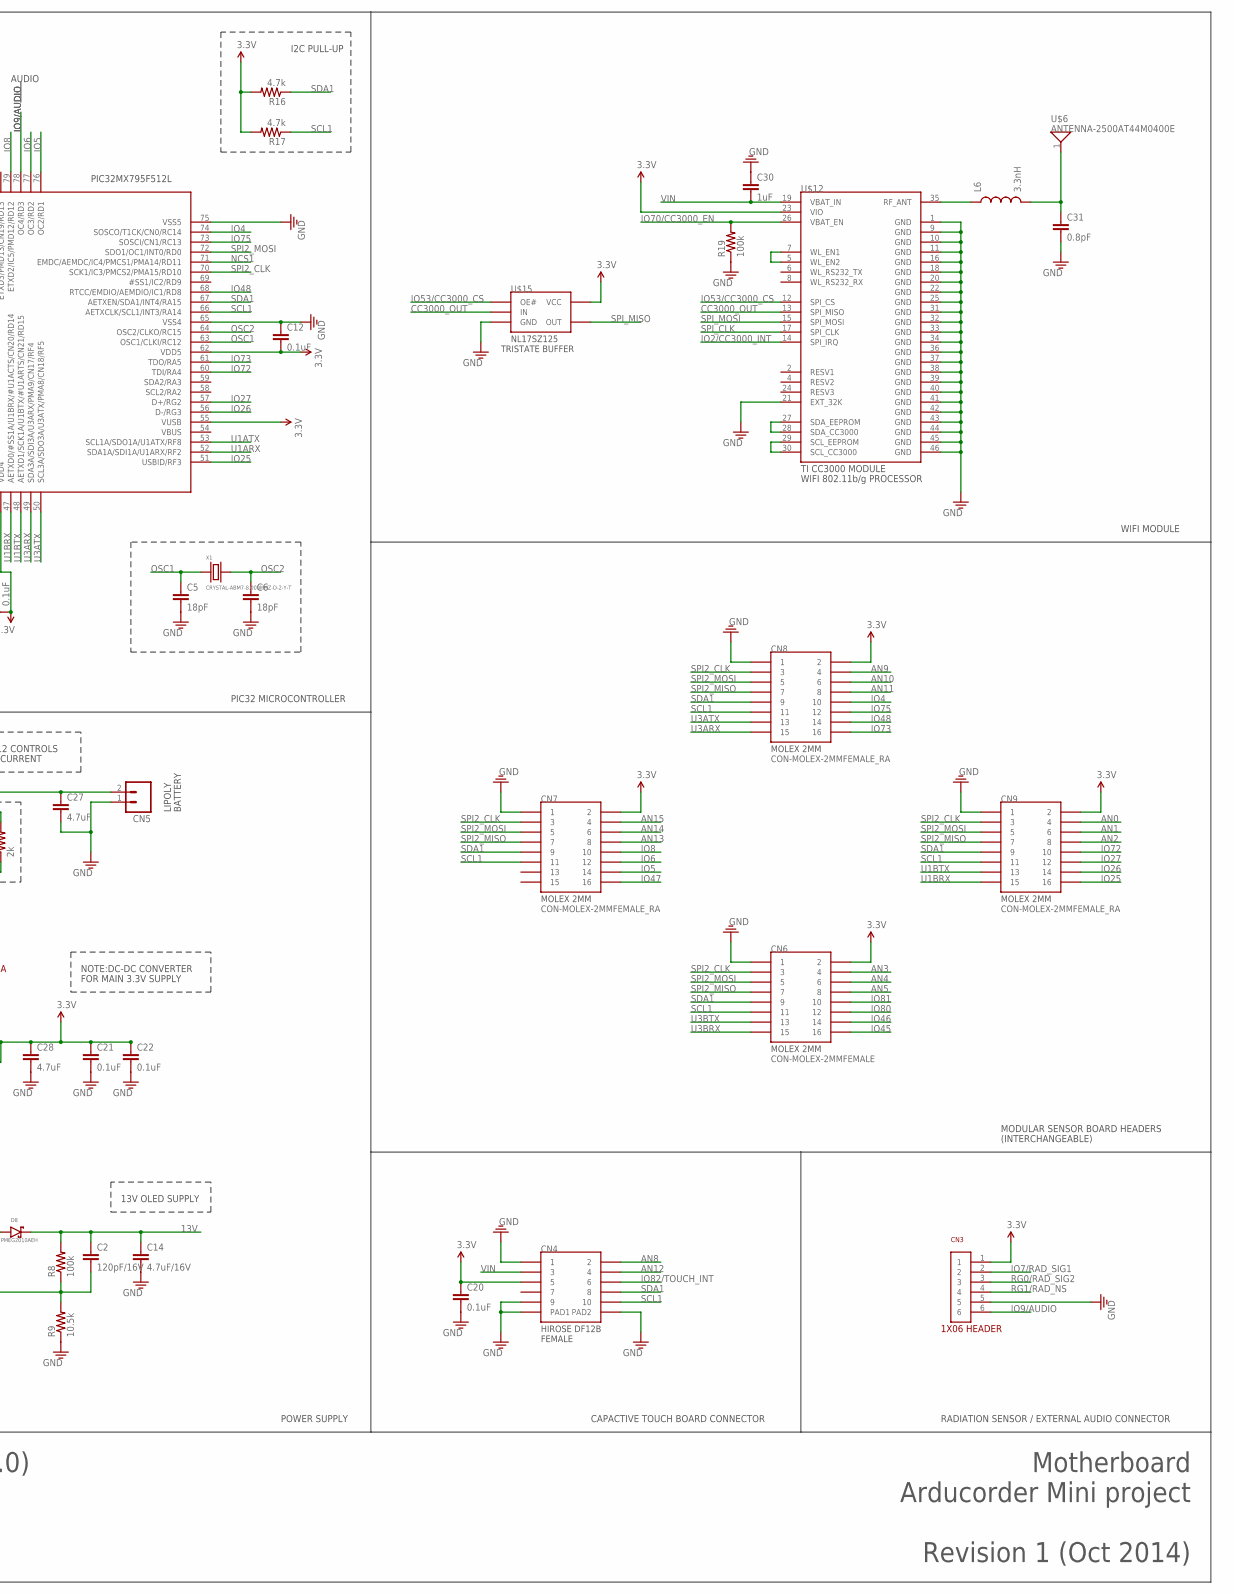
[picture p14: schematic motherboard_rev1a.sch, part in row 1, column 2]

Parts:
C1, C27, C28, C35, C48: 4.7uF; 0603
C2: 120pF/16V; 0603
C3, C4, C8, C9, C10, C11, C12, C13, C20, C21, C22: 0.1uF; 0603
C5, C6: 18pF; 0603
C7: 10uF; EIA3216
C14: 4.7uF/16V; 0603
C15: 4.7uF/25V; 0603
C16, C17, C18, C30: 1uF; 0603
C19: 0.1uF/16V; 0603
C31: 0.8pF; C0402
CN1: UG-2828GDEDF11-1.5OLED; XF2M-3015-1A-1.5LCD
CN2: 1X05
CN3: PHF-106-01-L-S; 1X06
CN4: FEMALE; DF12B(3.0)-10DP-0.5V(86)
CN5: M02-JST-2MM-SMT; JST-2-SMD
CN6: CON-MOLEX-2MMFEMALE; MOLEX-0791091007
CN7, CN8, CN9: CON-MOLEX-2MMFEMALE_RA; MOLEX-87368-1624
D1, D4, D5: 0605-LED; 0603-LED
D2, D3: UPS115UE3/TR7; DO-214BA
D8, D9, D10: PMEG2010AEH; SOD123F
L1: NR4018T100M
L3: INDUCTOR-SMD-VLF4012A; VLF4012A
L6: 3.3nH; C0402
R1, R2: 330; 0603
R3: 100; 0603
R4, R5: 1k; 0603
R6, R16, R17: 4.7k; 0603
R7, R11: 10k; 0603
R8, R10, R14, R19, R36: 100k; 0603
R9: 10.5k; 0603
R12: 2k; 0603
R13: 470; 0603
R15: 620k; 0603
R18: 51; 0603
SJ1: SOLDERJUMPERTRACE; SJ_2S-TRACE
U1: MCP73831; SOT23-5
U$2: TI-TPS63001-3.3V-BUCKBOOST; TPS63001
U$3: PIC32MX795F512L-80I/PF; SQFP-S-14X14-100
U$5: SWITCH_SPDT; KPS-1290
U$6: ANTENNA-2500AT44M0400E; ANT-2500AT44M0400E
U$7: CON-HIROSE-DM3B-MICROSD
U$8: USB-MICROB; FCI-10104110-0001LF
U$9: FT232RQ; QFN-32
U$12: CC3000
U$15: BUFFER-NL17SZ125; TSOP-5
U$24: FAN5331-BOOST; TSOP-5
X1: CRYSTAL-ABM7-8.000MHZ-D-2-Y-T; CYRSTAL-6.0X3.5MM

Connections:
3.3V: C1.1, C8.2, C9.1, C10.2, C11.2, C12.2, C13.1, C17.1, C18.2, C20.1, C21.1, C22.1, C28.1, CN1.4 (VDDIO), CN1.17 (BS0), CN1.18 (BS1), CN1.27 (VCI), CN2.2, CN3.1, CN4.5, CN6.2, CN7.2, CN8.2, CN9.2, L1.2, R10.1, R11.2, R16.2, R17.2, U$2.1 (VOUT), U$2.10 (FB), U$3.2 (VDD1), U$3.16 (VDD2), U$3.30 (AVDD), U$3.37 (VDD3), U$3.46 (VDD4), U$3.55 (VUSB), U$3.62 (VDD5), U$3.86 (VDD6), U$7.4 (VDD), U$9.1 (VCCIO), U$12.23 (VIO), U$15.5 (VCC), U$24.5 (VIN)
5V: C48.1, D2.ANODE, D4.ANODE, D5.ANODE, R6.2, R13.2, U1.4 (VIN), U$8.1 (VCC), U$9.19 (VCC)
13V: C2.1, C14.1, C19.1, CN1.2 (VCC), D8.1 (CATHODE), R8.2
AN0: CN9.4, U$3.25 (PGED1/AN0/CN2/RB0)
AN1: CN9.6, U$3.24 (PGEC1/AN1/CN3/RB1)
AN2: CN9.8, U$3.23 (AN2/C2IN-/CN4/RB2)
AN3: CN6.4, U$3.22 (AN3/C2IN+/CN5/RB3)
AN4: CN6.6, U$3.21 (AN4/C1IN-/CN6/RB4)
AN5: CN6.8, U$3.20 (AN5/C1IN+/VBUSON/CN7/RB5)
AN8: CN4.2, U$3.32 (AN8/C1OUT/RB8)
AN9: CN8.4, U$3.33 (AN9/C2OUT/RB9)
AN10: CN8.6, U$3.34 (AN10/CVREFOUT/PMA13/RB10)
AN11: CN8.8, U$3.35 (AN11/ERXERR/AETXERR/PMA12/RB11)
AN12: CN4.4, U$3.41 (AN12/ERXD0/AECRS/PMA11/RB12)
AN13: CN7.8, U$3.42 (AN13/ERXD1/AECOL/PMA10/RB13)
AN14: CN7.6, U$3.43 (AN14/ERXD2/AETXD3/PMALH/PMA1/RB14)
AN15: CN7.4, U$3.44 (AN15/ERXD3/AETXD2/OCFB/PMALL/PMA0/CN12/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)
CC3000_OUT: U$12.13 (SPI_MISO), U$15.2 (IN)
CHARGE_SENSE: D1.ANODE, R13.1
D0: CN1.14 (DB0), U$3.93 (PMD0/RE0)
D1: CN1.13 (DB1), U$3.94 (PMD1/RE1)
D2: CN1.12 (DB2), U$3.98 (PMD2/RE2)
D3: CN1.11 (DB3), U$3.99 (PMD3/RE3)
D4: CN1.10 (DB4), U$3.100 (PMD4/RE4)
D5: CN1.9 (DB5), U$3.3 (PMD5/RE5)
D6: CN1.8 (DB6), U$3.4 (PMD6/RE6)
D7: CN1.7 (DB7), U$3.5 (PMD7/RE7)
EN_REG: R36.2, U$2.6 (EN), U$5.O
GND: C1.2, C4.2, C5.2, C6.2, C7.C (-), C8.1, C9.2, C10.1, C11.1, C12.1, C13.2, C14.2, C15.2, C16.2, C17.2, C18.1, C19.2, C20.2, C21.2, C22.2, C27.2, C28.2, C30.1, C31.2, C35.2, C48.2, CN1.1 (GND1), CN1.28 (VSS), CN1.30 (GND2), CN1.PAD1, CN1.PAD2, CN2.3, CN3.5, CN4.1, CN4.9, CN4.PAD1, CN4.PAD2, CN5.1 (2), CN6.1, CN7.1, CN8.1, CN9.1, D10.1 (CATHODE), R7.1, R9.1, R12.1, R14.1, R15.1, R19.1, R36.1, U1.2 (VSS), U$2.3 (PGND), U$2.9 (GND), U$2.TH1 (THERM1), U$2.TH2 (THERM2), U$2.TH3 (THERM3), U$2.TH4 (THERM4), U$3.15 (VSS1), U$3.31 (AVSS), U$3.36 (VSS2), U$3.45 (VSS3), U$3.65 (VSS4), U$3.75 (VSS5), U$7.6 (GND), U$7.9 (CDET1), U$8.5 (GND), U$8.S1 (SH1), U$8.S2 (SH2), U$8.S3 (SH3), U$8.S4 (SH4), U$9.4 (GND), U$9.17 (GND), U$9.20 (GND), U$9.24 (AGND), U$9.26 (TEST), U$12.1 (GND), U$12.9 (GND), U$12.10 (GND), U$12.11 (GND), U$12.16 (GND), U$12.18 (GND), U$12.20 (GND), U$12.21 (EXT_32K), U$12.22 (GND), U$12.25 (GND), U$12.31 (GND), U$12.32 (GND), U$12.33 (GND), U$12.34 (GND), U$12.36 (GND), U$12.37 (GND), U$12.38 (GND), U$12.39 (GND), U$12.40 (GND), U$12.41 (GND), U$12.42 (GND), U$12.43 (GND), U$12.44 (GND), U$12.45 (GND), U$12.46 (GND), U$15.3 (GND), U$24.2 (GND)
IO2/CC3000_INT: U$3.18 (AERXD0/INT1/RE8), U$12.14 (SPI_IRQ)
IO4: CN8.10, U$3.74 (SOSCO/T1CK/CN0/RC14)
IO5: CN7.14, U$3.76 (OC2/RD1)
IO6: CN7.12, U$3.77 (OC3/RD2)
IO7/RAD_SIG1: CN3.2, U$3.19 (AERXD1/INT2/RE9)
IO8: CN7.10, U$3.79 (ETXD2/IC5/PMD12/RD12)
IO9/AUDIO: CN3.6, U$3.78 (OC4/RD3)
IO22/OLED_REG: CN1.20 (D/C#), U$3.7 (T3CK/RC2)
IO23/OLED_RESET: CN1.21 (RESET#), U$3.8 (T4CK/RC3)
IO25: CN9.16, U$3.51 (USBID/RF3)
IO26: CN9.14, U$3.56 (D-/RG3)
IO27: CN9.12, U$3.57 (D+/RG2)
IO28/OLED_BOOST_EN: R14.2, U$3.1 (AERXERR/RG15), U$24.4 (SHDN#)
IO45: CN6.16, U$3.87 (ETXD1/PMD11/RF0)
IO46: CN6.14, U$3.88 (ETXD0/PMD10/RF1)
IO47: CN7.16, U$3.83 (ETXEN/PMD14/CN15/RD6)
IO48: CN8.14, U$3.68 (RTCC/EMDIO/AEMDIO/IC1/RD8)
IO53/CC3000_CS: U$3.14 (ETHERNET/#SS2A/U2BRX/#U2ACTS/PMA2/CN11/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), U$12.12 (SPI_CS), U$15.1 (OE#)
IO70/CC3000_EN: R19.2, U$3.17 (TMS/RA0), U$12.26 (VBAT_EN)
IO72: CN9.10, U$3.60 (TDI/RA4)
IO73: CN8.16, U$3.61 (TDO/RA5)
IO75: CN8.12, U$3.73 (SOSCI/CN1/RC13)
IO80: CN6.12, U$3.91 (TRCLK/RA6)
IO81: CN6.10, U$3.92 (TRD3/RA7)
IO82/TOUCH_INT: CN4.6, U$3.95 (TRD2/RG14)
IO83/SD_CDET: R10.2, U$3.96 (TRD1/RG12), U$7.10 (CDET2)
IO84/CS_SD: U$3.97 (TRD0/RG13), U$7.2 (CD/DAT3)
MCLR#: CN2.1, R11.1, SJ1.2, U$3.13 (#MCLR)
unnamed: L3.1, U$2.4 (L1)
unnamed: L3.2, U$2.2 (L2)
unnamed: U$8.2 (D-), U$9.15 (USBDM)
unnamed: U$8.3 (D+), U$9.14 (USBDP)
unnamed: R1.1, U$9.22 (TXLED)
unnamed: R2.1, U$9.21 (RXLED)
unnamed: D4.CATHODE, R1.2
unnamed: D5.CATHODE, R2.2
unnamed: C3.1, U$9.31 (DTR)
unnamed: R3.1, U$9.32 (RTS)
unnamed: C3.2, R3.2, SJ1.1
unnamed: C4.1, R6.1, R7.2, U$9.18 (RESET)
unnamed: R5.1, U$9.2 (RXD)
unnamed: C31.1, L6.2, U$6.1
unnamed: R4.1, U$9.30 (TXD)
unnamed: U$12.27 (SDA_EEPROM), U$12.28 (SDA_CC3000)
unnamed: L6.1, U$12.35 (RF_ANT)
unnamed: C7.A (+), U$3.85 (VCAP/VDDCORE)
unnamed: C15.1, CN1.3 (VCOMH)
unnamed: D8.2 (ANODE), L1.1, U$24.1 (SW)
unnamed: CN1.22 (IREF), R15.2
unnamed: C2.2, R8.1, R9.2, U$24.3 (FB)
unnamed: C16.1, CN1.26 (VDD)
unnamed: D9.1 (CATHODE), D10.2 (ANODE)
unnamed: D9.2 (ANODE), R18.1
unnamed: R12.2, U1.5 (PROG)
unnamed: U$12.29 (SCL_EEPROM), U$12.30 (SCL_CC3000)
unnamed: CN1.5 (VSL), R18.2
unnamed: D1.CATHODE, U1.1 (STAT)
unnamed: U$12.5 (WL_EN2), U$12.7 (WL_EN1)
NCS1: CN1.19 (CS#), U$3.71 (EMDC/AEMDC/IC4/PMCS1/PMA14/RD11)
NRD: CN1.15 (E/RD#), U$3.82 (PMRD/CN14/RD5)
NWR: CN1.16 (R/W#), U$3.81 (OC5/PMWR/CN13/RD4)
OSC1: C5.1, U$3.63 (OSC1/CLKI/RC12), X1.1
OSC2: C6.1, U$3.64 (OSC2/CLKO/RC15), X1.2
PGEC2: CN2.5, U$3.26 (PGEC2/AN6/OCFA/RB6)
PGED2: CN2.4, U$3.27 (PGED2/AN7/RB7)
RG0/RAD_SIG2: CN3.3, U$3.90 (PMD8/RG0)
RG1/RAD_NS: CN3.4, U$3.89 (ETXERR/PMD9/RG1)
SCL1: CN4.10, CN6.11, CN7.11, CN8.11, CN9.11, R17.1, U$3.66 (AETXCLK/SCL1/INT3/RA14)
SDA1: CN4.8, CN6.9, CN7.9, CN8.9, CN9.9, R16.1, U$3.67 (AETXEN/SDA1/INT4/RA15)
SPI2_CLK: CN6.3, CN7.3, CN8.3, CN9.3, U$3.70 (SCK1/IC3/PMCS2/PMA15/RD10)
SPI2_MISO: CN6.7, CN7.7, CN8.7, CN9.7, U$3.9 (T5CK/SDI1/RC4)
SPI2_MOSI: CN6.5, CN7.5, CN8.5, CN9.5, U$3.72 (SDO1/OC1/INT0/RD0)
SPI_CLK: U$3.10 (ECOL/SCK2A/U2BTX/#U2ARTS/PMA5/CN8/RG6), U$7.5 (CLK), U$12.17 (SPI_CLK)
SPI_MISO: U$3.11 (ECRS/SDA2A/SDI2A/U2ARX/PMA4/CN9/RG7), U$7.7 (DAT0), U$15.4 (OUT)
SPI_MOSI: U$3.12 (ETHERNET/SCL2A/SDO2A/U2ATX/PMA3/CN10/RG8), U$7.3 (CMD), U$12.15 (SPI_MOSI)
U1ARX: R4.2, U$3.52 (SDA1A/SDI1A/U1ARX/RF2)
U1ATX: R5.2, U$3.53 (SCL1A/SDO1A/U1ATX/RF8)
U1BRX: CN9.15, U$3.47 (AETXD0/#SS1A/U1BRX/#U1ACTS/CN20/RD14)
U1BTX: CN9.13, U$3.48 (AETXD1/SCK1A/U1BTX/#U1ARTS/CN21/RD15)
U3ARX: CN8.15, U$3.49 (SDA3A/SDI3A/U3ARX/PMA9/CN17/RF4)
U3ATX: CN8.13, U$3.50 (SCL3A/SDO3A/U3ATX/PMA8/CN18/RF5)
U3BRX: CN6.15, U$3.40 (#SS3A/U3BRX/#U3ACTS/RF12)
U3BTX: CN6.13, U$3.39 (SCK3A/U3BTX/#U3ARTS/RF13)
VBAT: C27.1, CN5.2 (1), D3.ANODE, U1.3 (VBAT)
VIN: C30.2, C35.1, CN4.3, D2.CATHODE, D3.CATHODE, U$2.5 (VIN), U$2.7 (PS/SYNC), U$2.8 (VINA), U$5.P, U$12.19 (VBAT_IN)

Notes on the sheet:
NOTE: R12 CONTROLS
CHARGE CURRENT
POWER SELECTION
SCHOTTKY O-RING
USE LOW DROPOUT
UPS115UE3/TR7
DIODES
LIPOLY
POWER SWITCH
AUDIO
Released under the Creative Commons Attribution-ShareAlike 4.0 International (CC BY-SA 4.0)
http://creativecommons.org/licenses/by-sa/4.0/
Designed by: Peter Jansen
http://www.tricorderproject.org
Revision 1 (Oct 2014)
Arducorder Mini project
Motherboard
USB-TO-SERIAL
MICRO SD CARD CONNECTOR
OLED DISPLAY
PIC32 MICROCONTROLLER
POWER SUPPLY
LIPOLY CHARGER
NOTE:DC-DC CONVERTER
FOR MAIN 3.3V SUPPLY
13V OLED SUPPLY
BATTERY
WIFI MODULE
MODULAR SENSOR BOARD HEADERS
(INTERCHANGEABLE)
CAPACTIVE TOUCH BOARD CONNECTOR
RADIATION SENSOR / EXTERNAL AUDIO CONNECTOR
ICD3 PROGRAMMING HEADER
I2C PULL-UP

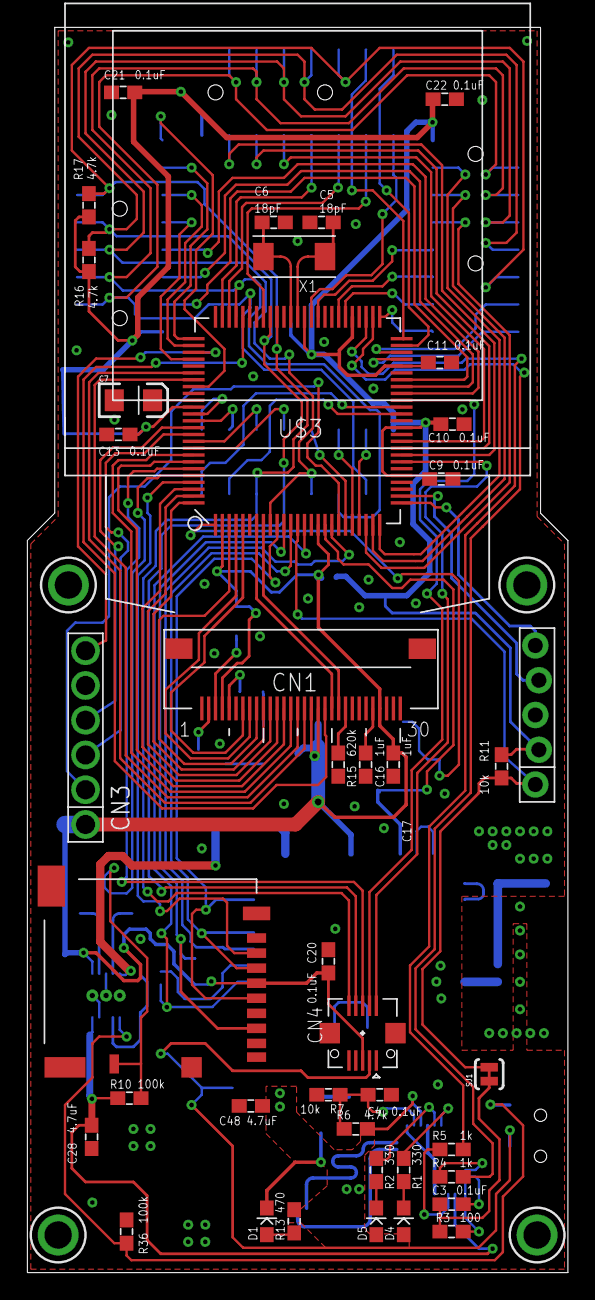
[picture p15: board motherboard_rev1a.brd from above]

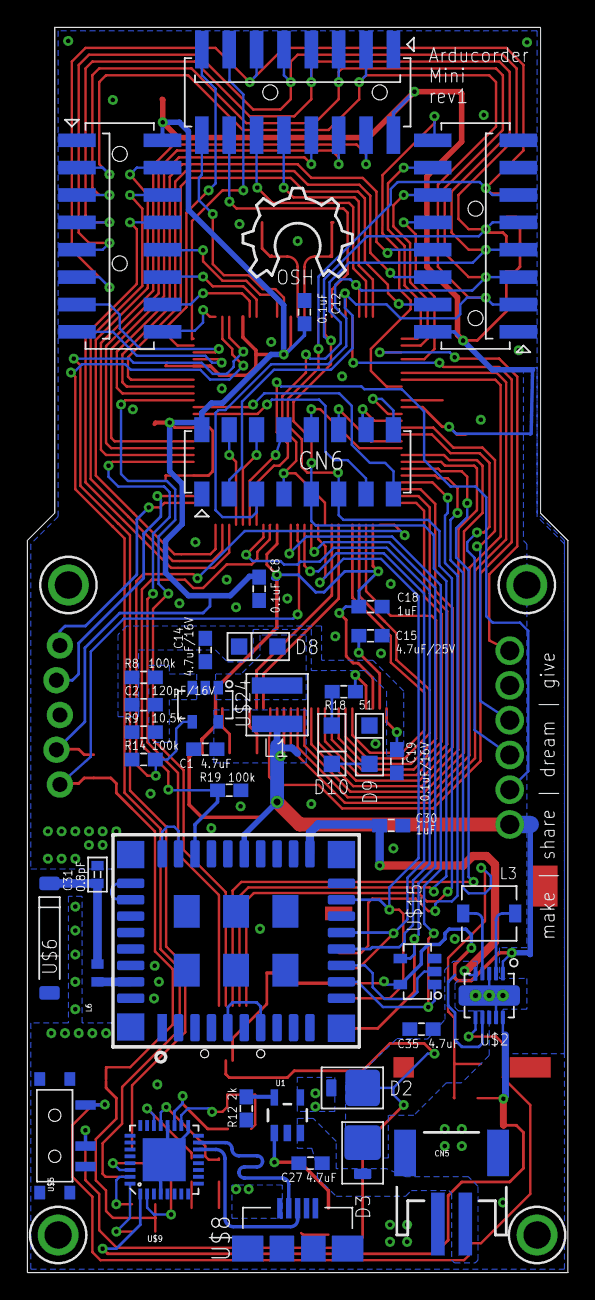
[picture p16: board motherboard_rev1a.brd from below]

Board: 2 copper layers, 39.5 x 91.0 mm, 81 parts (40 on the bottom side), 114 nets.

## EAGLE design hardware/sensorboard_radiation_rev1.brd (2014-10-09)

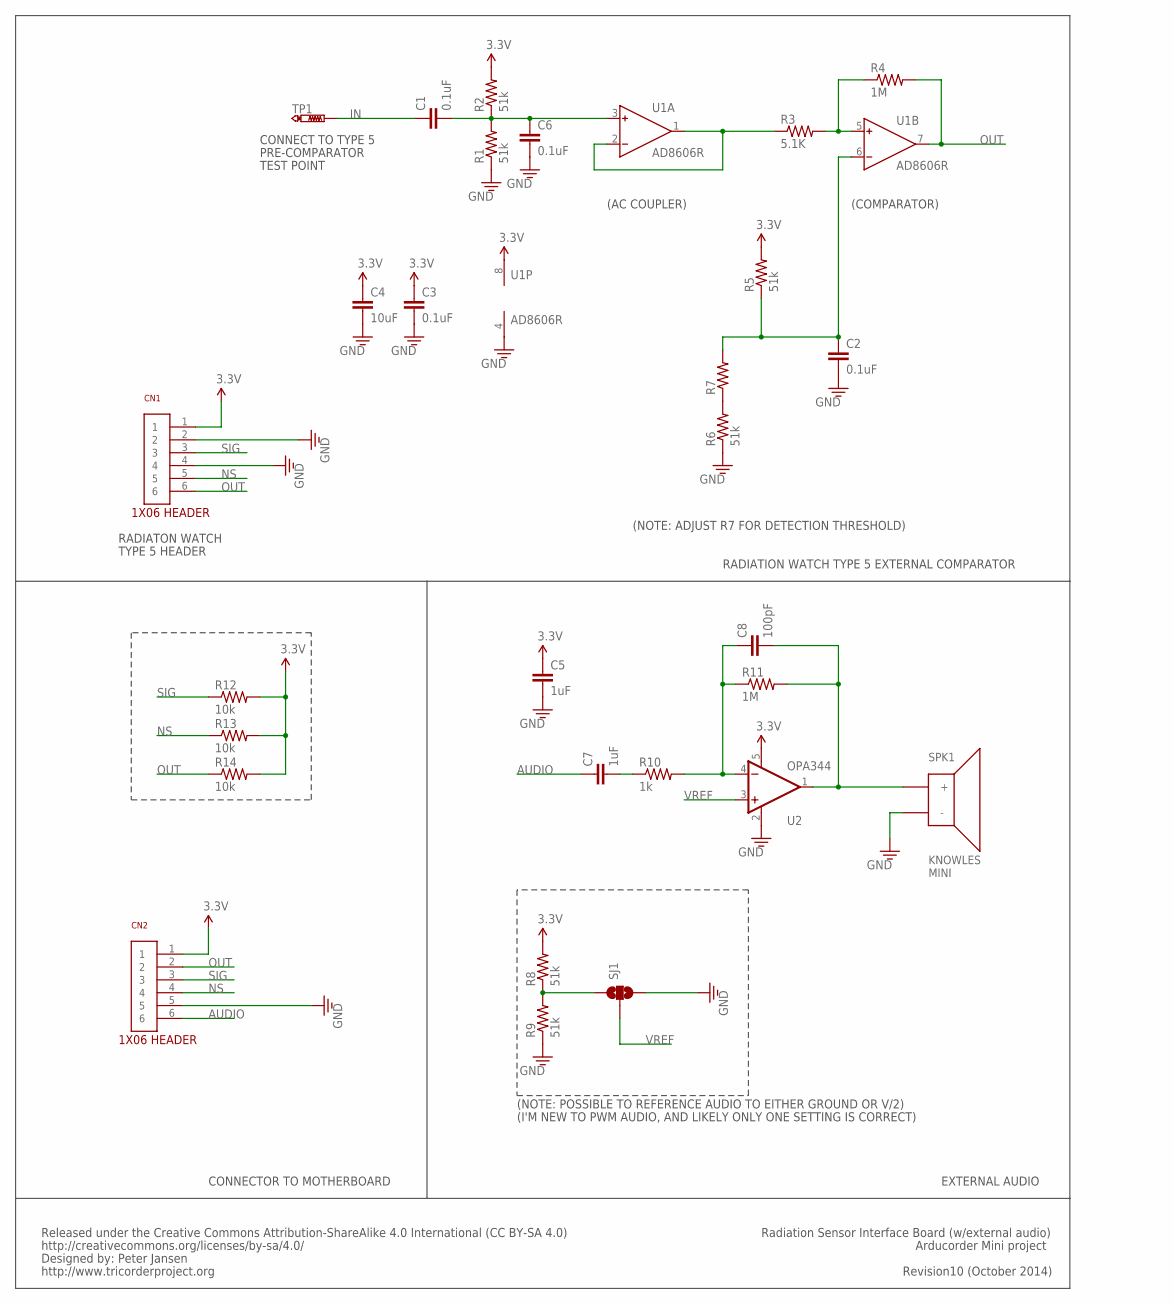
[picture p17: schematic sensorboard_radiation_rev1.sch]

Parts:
C1, C2, C3, C6: 0.1uF; 0603
C4: 10uF; 0603
C5, C7: 1uF; 0603
C8: 100pF; 0603
CN1: 1X06
CN2: PHT-106-01-L-S; 1X06
R1, R2, R5, R6, R8, R9: 51k; 0603
R3: 5.1K; 0603
R4, R11: 1M; 0603
R7: RESISTOR0603; 0603
R10: 1k; 0603
R12, R13, R14: 10k; 0603
SJ1: SOLDERJUMPER_2WAYPASTE1&2; SJ_3_PASTE1&2
SPK1: KNOWLES-MINI-SPEAKER
TP1: PTR1PAD1-13; P1-13
U1: AD8606R; SO8
U2: OPA344; SOT23-5

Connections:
3.3V: C3.1, C4.1, C5.1, CN1.1, CN2.1, R2.2, R5.2, R8.2, R12.2, R13.2, R14.2, U1.8 (V+), U2.5 (V+)
ADMP_OUT: C8.2, R11.2, SPK1.POS (+), U2.1 (OUT)
AUDIO: C7.1, CN2.6
GND: C2.2, C3.2, C4.2, C5.2, C6.2, CN1.2, CN1.4, CN2.5, R1.1, R6.1, R9.1, SJ1.3, SPK1.NEG (-), U1.4 (V-), U2.2 (V-)
IN: C1.1, TP1.TP
unnamed: R6.2, R7.1
unnamed: C1.2, C6.1, R1.2, R2.1, U1.3 (IN+)
unnamed: R3.1, U1.1 (OUT), U1.2 (IN-)
unnamed: R3.2, R4.1, U1.5 (IN+)
unnamed: C2.1, R5.1, R7.2, U1.6 (IN-)
unnamed: C7.2, R10.1
unnamed: C8.1, R10.2, R11.1, U2.4 (-IN)
NS: CN1.5, CN2.4, R13.1
OUT: CN1.6, CN2.2, R4.2, R14.1, U1.7 (OUT)
SIG: CN1.3, CN2.3, R12.1
VREF: SJ1.2, U2.3 (+IN)
VREF1: R8.1, R9.2, SJ1.1

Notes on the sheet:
(AC COUPLER)
(COMPARATOR)
CONNECT TO TYPE 5
PRE-COMPARATOR
TEST POINT
RADIATON WATCH
TYPE 5 HEADER
(NOTE: ADJUST R7 FOR DETECTION THRESHOLD)
(NOTE: POSSIBLE TO REFERENCE AUDIO TO EITHER GROUND OR V/2)
Released under the Creative Commons Attribution-ShareAlike 4.0 International (CC BY-SA 4.0)
http://creativecommons.org/licenses/by-sa/4.0/
Designed by: Peter Jansen
http://www.tricorderproject.org
Revision10 (October 2014)
Arducorder Mini project
Radiation Sensor Interface Board (w/external audio)
(I'M NEW TO PWM AUDIO, AND LIKELY ONLY ONE SETTING IS CORRECT)
EXTERNAL AUDIO
CONNECTOR TO MOTHERBOARD
RADIATION WATCH TYPE 5 EXTERNAL COMPARATOR

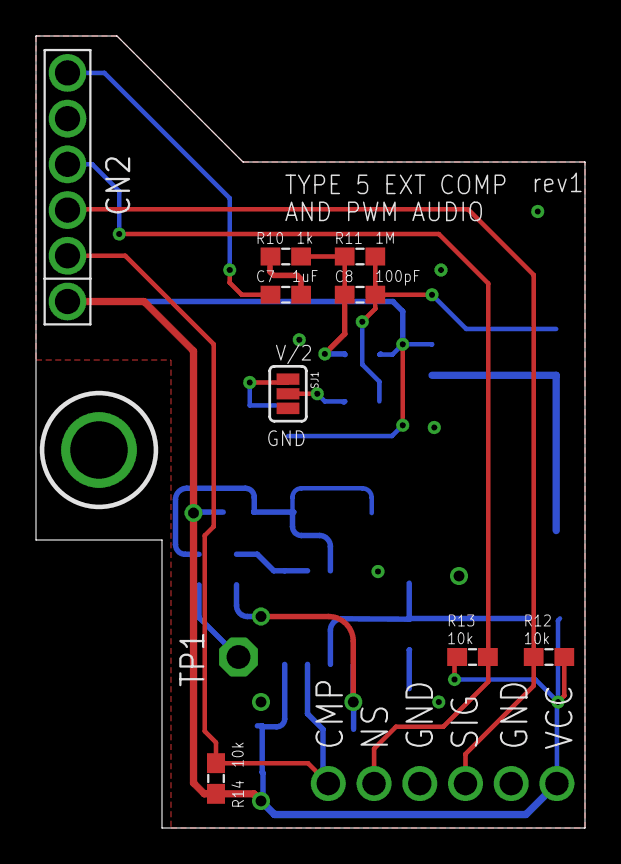
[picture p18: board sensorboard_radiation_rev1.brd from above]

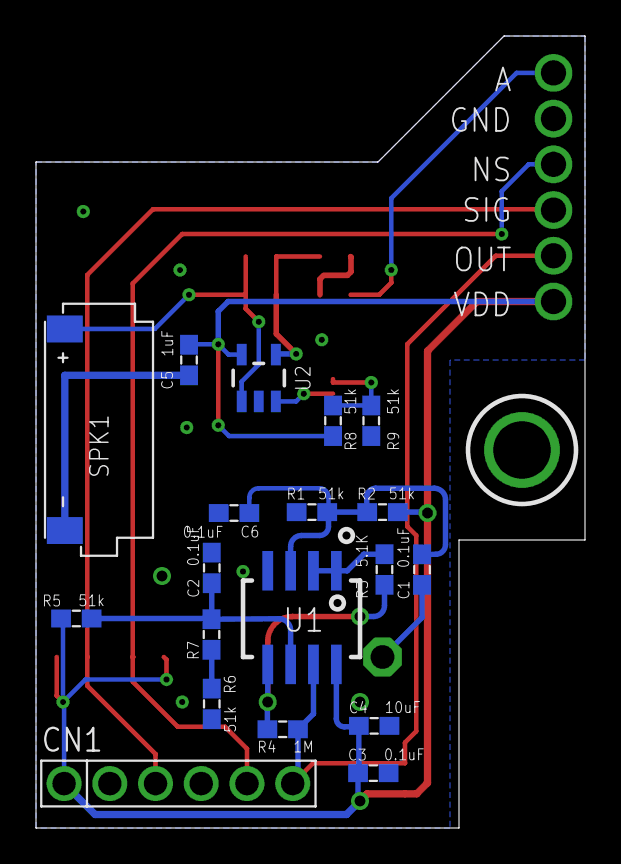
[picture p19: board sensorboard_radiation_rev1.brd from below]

Board: 2 copper layers, 30.5 x 44.0 mm, 29 parts (19 on the bottom side), 17 nets.

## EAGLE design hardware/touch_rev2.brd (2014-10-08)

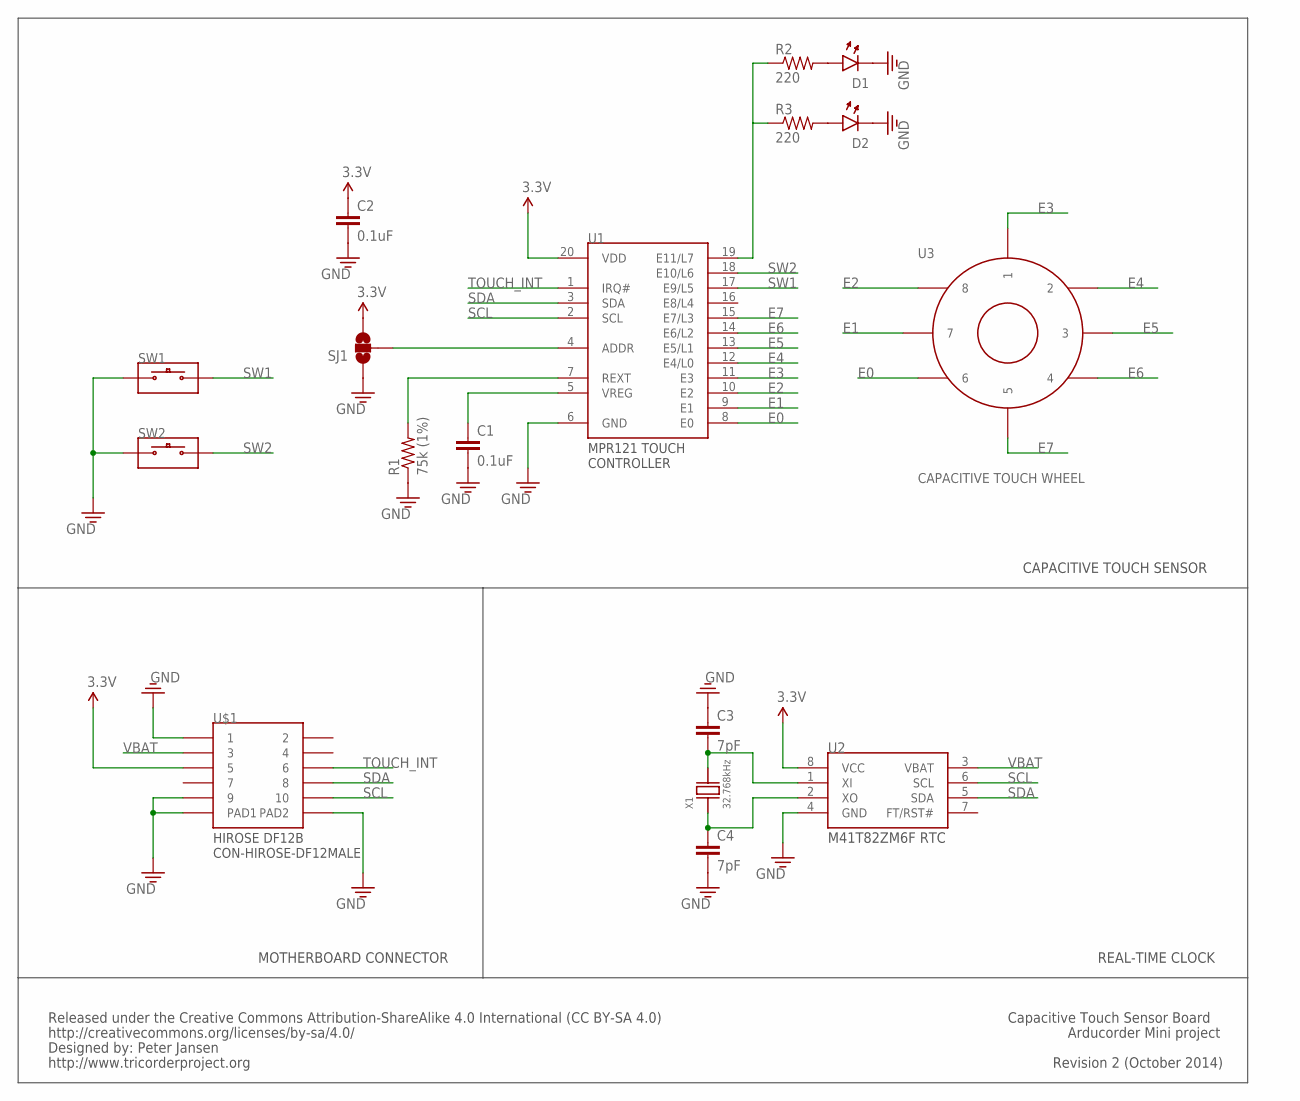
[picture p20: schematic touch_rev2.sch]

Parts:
C1, C2: 0.1uF; 0603
C3, C4: 7pF; 0603
D1, D2: 0605-LED; 0603-LED
R1: 75k (1%); 0603
R2, R3: 220; 0603
SJ1: SOLDERJUMPER_2WAYPASTE1&2; SJ_3_PASTE1&2
SW1, SW2: SWITCH; KMT071
U1: MPR121-TOUCH-CONTROLLER; QFN-3X3-20
U2: M41T82ZM6F; 8-SOIC
U3: CAPACITIVE-WHEEL-8
U$1: CON-HIROSE-DF12MALE; DF12B(3.0)-10DS-0.5V(86)
X1: 32.768kHz; CRYSTAL-9HT10

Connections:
3.3V: C2.1, SJ1.3, U1.20 (VDD), U2.8 (VCC), U$1.5
E0: U1.8 (E0), U3.6
E1: U1.9 (E1), U3.7
E2: U1.10 (E2), U3.8
E3: U1.11 (E3), U3.1
E4: U1.12 (E4/L0), U3.2
E5: U1.13 (E5/L1), U3.3
E6: U1.14 (E6/L2), U3.4
E7: U1.15 (E7/L3), U3.5
GND: C1.2, C2.2, C3.1, C4.2, D1.CATHODE, D2.CATHODE, R1.1, SJ1.1, SW1.1A, SW2.1A, U1.6 (GND), U2.4 (GND), U$1.1, U$1.9, U$1.PAD1, U$1.PAD2
unnamed: D1.ANODE, R2.2
unnamed: D2.ANODE, R3.2
unnamed: C1.1, U1.5 (VREG)
unnamed: R1.2, U1.7 (REXT)
unnamed: SJ1.2, U1.4 (ADDR)
unnamed: R2.1, R3.1, U1.19 (E11/L7)
unnamed: C4.1, U2.2 (XO), X1.1
unnamed: C3.2, U2.1 (XI), X1.2
SCL: U1.2 (SCL), U2.6 (SCL), U$1.10
SDA: U1.3 (SDA), U2.5 (SDA), U$1.8
SW1: SW1.2A, U1.17 (E9/L5)
SW2: SW2.2A, U1.18 (E10/L6)
TOUCH_INT: U1.1 (IRQ#), U$1.6
VBAT: U2.3 (VBAT), U$1.3

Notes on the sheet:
CAPACITIVE TOUCH SENSOR
REAL-TIME CLOCK
MOTHERBOARD CONNECTOR
Released under the Creative Commons Attribution-ShareAlike 4.0 International (CC BY-SA 4.0)
http://creativecommons.org/licenses/by-sa/4.0/
Designed by: Peter Jansen
http://www.tricorderproject.org
Revision 2 (October 2014)
Arducorder Mini project
Capacitive Touch Sensor Board

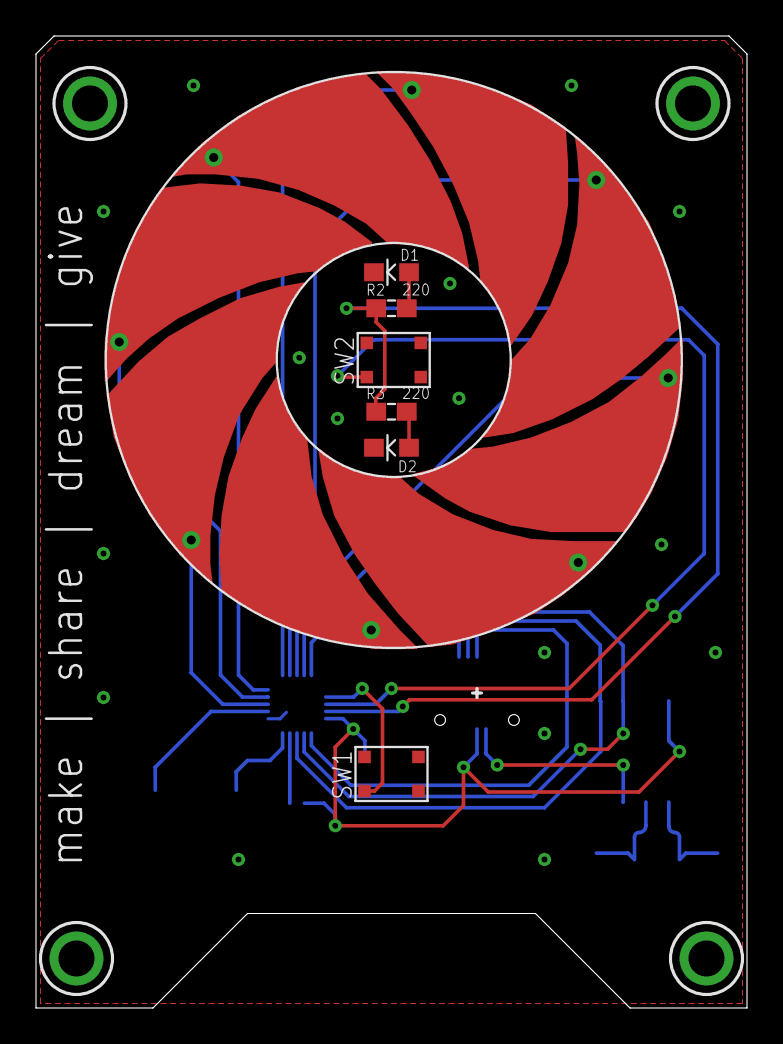
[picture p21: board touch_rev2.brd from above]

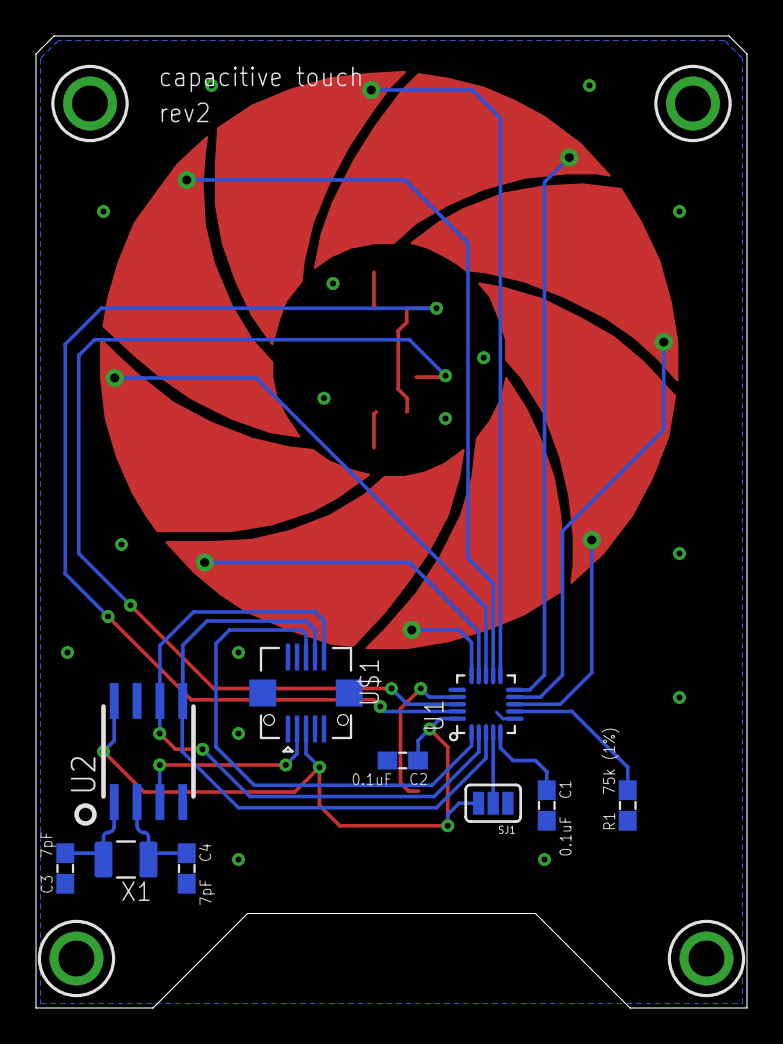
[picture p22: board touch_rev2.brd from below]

Board: 2 copper layers, 39.5 x 54.0 mm, 17 parts (9 on the bottom side), 24 nets.

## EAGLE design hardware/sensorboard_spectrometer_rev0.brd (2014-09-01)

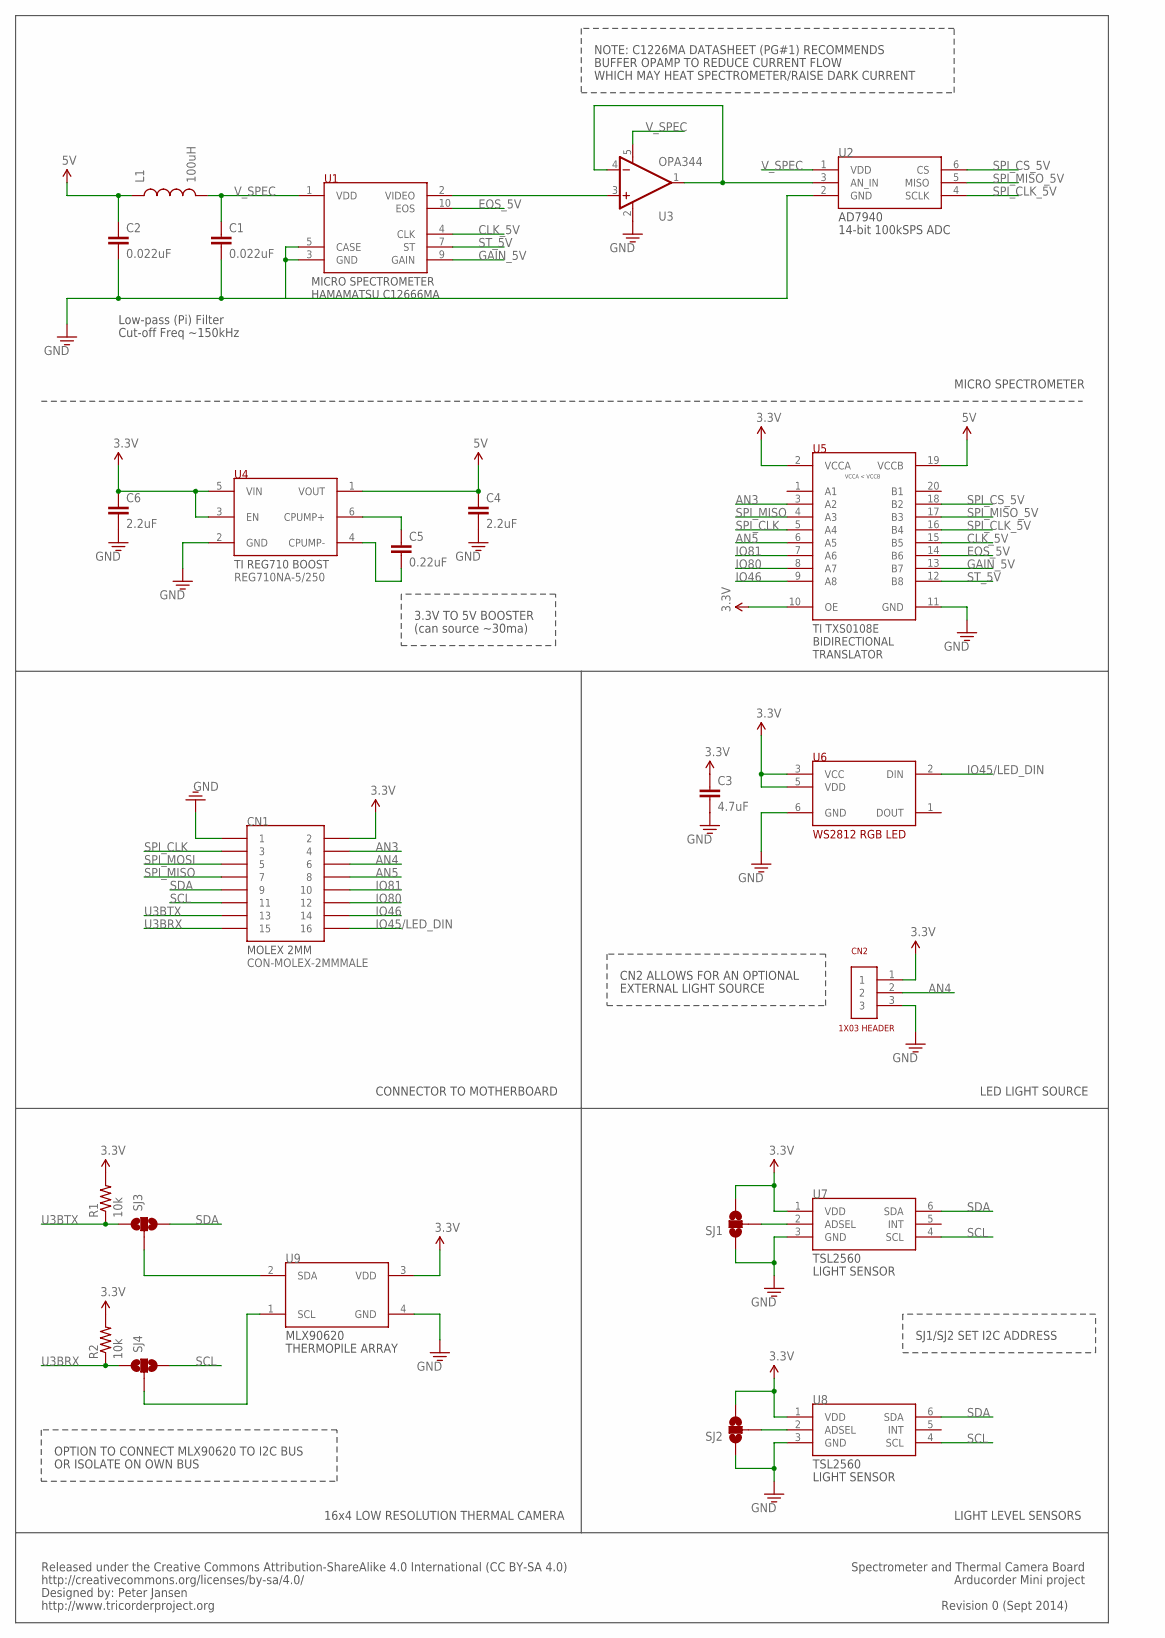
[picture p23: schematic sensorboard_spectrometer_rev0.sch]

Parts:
C1, C2: 0.022uF; 0603
C3: 4.7uF; 0603
C4, C6: 2.2uF; 0603
C5: 0.22uF; 0603
CN1: CON-MOLEX-2MMMALE; MOLEX-0877591650
CN2: 1X03
L1: 100uH; 0805
R1, R2: 10k; 0603
SJ1, SJ3, SJ4: SOLDERJUMPER_2WAYPASTE1&2; SJ_3_PASTE1&2
SJ2: SOLDERJUMPER_2WAYPASTE2&3; SJ_3_PASTE2&3
U1: MICROSPEC-C12666MA; C12666MA
U2: AD7940; SOT-23-6L
U3: OPA344; SOT23-5
U4: REG710NA-5/250; SOT-23-6L
U5: TRANSLATOR-TXS0108E; TSSOP-20
U6: WS2812_NEOPIXEL; WS2812
U7, U8: TSL2561; TMB-6
U9: MLX90620

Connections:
3.3V: C3.1, C6.1, CN1.2, CN2.1, R1.2, R2.2, SJ1.3, SJ2.3, U4.3 (EN), U4.5 (VIN), U5.2 (VCCA), U5.10 (OE), U6.3 (VCC), U6.5 (VDD), U7.1 (VDD), U8.1 (VDD), U9.3 (VDD)
5V: C2.1, C4.1, L1.1, U4.1 (VOUT), U5.19 (VCCB)
AN3: CN1.4, U5.3 (A2)
AN4: CN1.6, CN2.2
AN5: CN1.8, U5.6 (A5)
CLK_5V: U1.4 (CLK), U5.15 (B5)
EOS_5V: U1.10 (EOS), U5.14 (B6)
GAIN_5V: U1.9 (GAIN), U5.13 (B7)
GND: C1.2, C2.2, C3.2, C4.2, C6.2, CN1.1, CN2.3, SJ1.1, SJ2.1, U1.3 (GND), U1.5 (CASE), U2.2 (GND), U3.2 (V-), U4.2 (GND), U5.11 (GND), U6.6 (GND), U7.3 (GND), U8.3 (GND), U9.4 (GND)
IO45/LED_DIN: CN1.16, U6.2 (DIN)
IO46: CN1.14, U5.9 (A8)
IO80: CN1.12, U5.8 (A7)
IO81: CN1.10, U5.7 (A6)
unnamed: U2.3 (AN_IN), U3.1 (OUT), U3.4 (-IN)
unnamed: U1.2 (VIDEO), U3.3 (+IN)
unnamed: SJ2.2, U8.2 (ADSEL)
unnamed: SJ1.2, U7.2 (ADSEL)
unnamed: C5.1, U4.6 (CPUMP+)
unnamed: C5.2, U4.4 (CPUMP-)
unnamed: SJ4.2, U9.1 (SCL)
unnamed: SJ3.2, U9.2 (SDA)
SCL: CN1.11, SJ4.3, U7.4 (SCL), U8.4 (SCL)
SDA: CN1.9, SJ3.3, U7.6 (SDA), U8.6 (SDA)
SPI_CLK: CN1.3, U5.5 (A4)
SPI_CLK_5V: U2.4 (SCLK), U5.16 (B4)
SPI_CS_5V: U2.6 (CS), U5.18 (B2)
SPI_MISO: CN1.7, U5.4 (A3)
SPI_MISO_5V: U2.5 (MISO), U5.17 (B3)
SPI_MOSI: CN1.5
ST_5V: U1.7 (ST), U5.12 (B8)
U3BRX: CN1.15, R2.1, SJ4.1
U3BTX: CN1.13, R1.1, SJ3.1
V_SPEC: C1.1, L1.2, U1.1 (VDD), U2.1 (VDD), U3.5 (V+)

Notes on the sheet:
Low-pass (Pi) Filter
Cut-off Freq ~150kHz
CONNECTOR TO MOTHERBOARD
LED LIGHT SOURCE
16x4 LOW RESOLUTION THERMAL CAMERA
LIGHT LEVEL SENSORS
3.3V TO 5V BOOSTER
(can source ~30ma)
MICRO SPECTROMETER
NOTE: C1226MA DATASHEET (PG#1) RECOMMENDS
BUFFER OPAMP TO REDUCE CURRENT FLOW
WHICH MAY HEAT SPECTROMETER/RAISE DARK CURRENT
CN2 ALLOWS FOR AN OPTIONAL
EXTERNAL LIGHT SOURCE
OPTION TO CONNECT MLX90620 TO I2C BUS
OR ISOLATE ON OWN BUS
SJ1/SJ2 SET I2C ADDRESS
Released under the Creative Commons Attribution-ShareAlike 4.0 International (CC BY-SA 4.0)
http://creativecommons.org/licenses/by-sa/4.0/
Designed by: Peter Jansen
http://www.tricorderproject.org
Revision 0 (Sept 2014)
Arducorder Mini project
Spectrometer and Thermal Camera Board

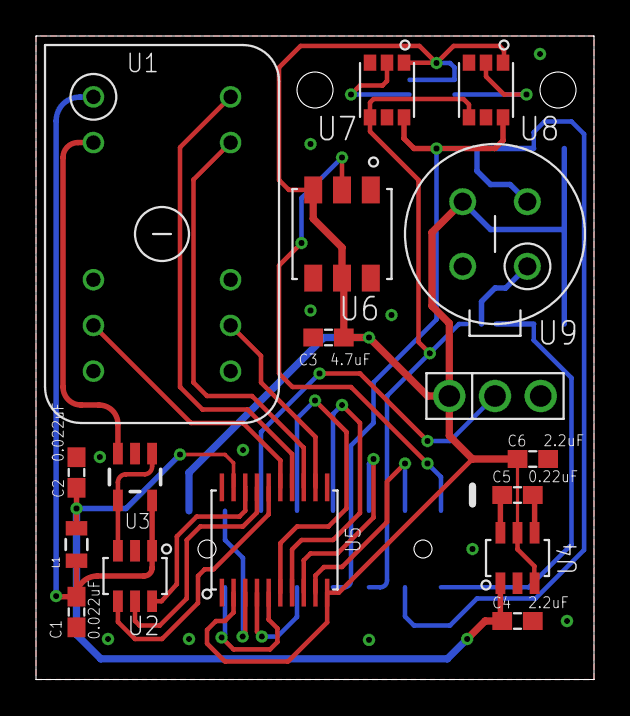
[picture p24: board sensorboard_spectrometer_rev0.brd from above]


Board: 2 copper layers, 31.0 x 35.8 mm, 24 parts (7 on the bottom side), 32 nets.

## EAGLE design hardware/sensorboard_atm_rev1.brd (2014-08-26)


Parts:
C1, C2: 0.1uF; 0603
CN1: CON-MOLEX-2MMMALE; MOLEX-0877591650
R1: 541; 0603
R2: 18; 0603
R3: 86; 0603
R4, R5, R6: 56k; 0603
R7, R8, R9: 1k; 0603
R10, R11, R12: 100k; 0603
U1: BMP180
U2: HTU21D
U3: MICS-6814
U4, U5, U6: MOSFET-IRLML6401; SOT23-3L

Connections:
3.3V: C1.1, C2.1, CN1.2, R4.2, R5.2, R6.2, R10.2, R11.2, R12.2, U1.2 (VDD), U1.3 (VDDIO), U2.5 (VDD), U4.2 (S), U5.2 (S), U6.2 (S)
CO_R: CN1.6, R5.1, U3.H (RS2_RED)
GND: C1.2, C2.2, CN1.1, U1.7 (GND), U2.2 (GND1), U2.PAD (GND2), U3.B (RH1/RS1_RED), U3.F (RS2_NH3), U3.J (RH1/RS1_OX)
MICS_H1: R1.1, R10.1, U4.1 (G)
MICS_H1_EN: CN1.12, R7.1
MICS_H2: R2.2, R11.1, U5.1 (G)
MICS_H2_EN: CN1.14, R8.1
MICS_H3: R3.2, R12.1, U6.1 (G)
MICS_H3_EN: CN1.16, R9.1
unnamed: R7.2, U4.3 (D)
unnamed: R8.2, U5.3 (D)
unnamed: R9.2, U6.3 (D)
unnamed: R1.2, U3.E (RH2_NH3), U3.G (RH2_RED)
unnamed: R2.1, U3.C (RH1_NH3)
unnamed: R3.1, U3.K (RH2_OX)
NH3_R: CN1.4, R4.1, U3.D (RS1_NH3)
NO2_R: CN1.8, R6.1, U3.A (RS2)
SCL: CN1.11, U1.5 (SCL), U2.6 (SCL)
SDA: CN1.9, U1.6 (SDA), U2.1 (SDA)

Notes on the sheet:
(I2C_ADDR: 0x77)
VOLTAGE DIVIDERS FOR
MEASURING GAS SENSOR
RESISTANCE
(I2C_ADDR: 0x40)
Released under the Creative Commons Attribution-ShareAlike 4.0 International (CC BY-SA 4.0)
http://creativecommons.org/licenses/by-sa/4.0/
Designed by: Peter Jansen
http://www.tricorderproject.org
Revision 1 (August 2014)
Arducorder Mini project
Atmospheric Temperature, Pressure, Humidity, and Gas Sensor Board
CONNECTOR TO MOTHERBOARD
NOTE: SEE PG#3 OF MICS6814
DATASHEET. R1, R2, AND R3
RECALCUATED FOR 3.3V SUPPLY
GAS SENSOR
HUMIDITY SENSOR
PRESSURE SENSOR



Board: 2 copper layers, 15.0 x 25.0 mm, 21 parts (7 on the bottom side), 19 nets.

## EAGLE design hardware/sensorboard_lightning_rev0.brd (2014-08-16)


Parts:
C1: 1nF; 0603
C2, C8: 100pF; 0603
C3, C6: 10uF; 0603
C4: 1uF; 0603
C5, C9: 0.1uF; 0603
C7: 4.7uF; 0603
CN1: CON-MOLEX-2MMMALE; MOLEX-0877591650
L1: MA5532 100uH; MA5532-AE
LED1: LED1206; LED-1206
R1, R5, R6: 10k; 0603
R2: 30; 0603
R3: 1.5k; 0603
R4: 100k; 0603
U1: AS3935; 16LD_MLPQ-(4X4MM)
U2: SI1145
U3: ADMP401
U4: OPA344; SOT23-5

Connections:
3.3V: C4.1, C5.2, C9.1, CN1.2, R2.2, R5.2, U1.5 (VDD), U1.6 (VREG), U1.9 (SI), U1.15 (ADD0), U1.16 (ADD1), U2.3 (VDD), U2.6 (LED2), U2.7 (LED3), U3.5 (VDD), U4.5 (V+)
ADMP_OUT: C8.2, CN1.6, R4.2, U4.1 (OUT)
AS3935_INT: CN1.10, U1.10 (IRQ)
GND: C1.2, C2.2, C3.1, C4.2, C5.1, C6.2, C9.2, CN1.1, L1.2, R1.1, R6.1, U1.2 (INN), U1.4 (GND), U1.7 (EN_VREG), U1.8 (CS), U1.12 (MISO), U1.PAD (GND_PAD), U2.8 (GND), U3.2 (GND), U3.4 (GND), U3.6 (GND), U4.2 (V-)
unnamed: LED1.C, U2.9 (LED1)
unnamed: C3.2, U1.1 (ACG)
unnamed: C6.1, LED1.A, R2.1
unnamed: C1.1, C2.1, L1.1, R1.2, U1.3 (INP)
unnamed: C7.2, R3.1
unnamed: C8.1, R3.2, R4.1, U4.4 (-IN)
unnamed: C7.1, U3.1 (OUT)
SCL: CN1.11, U1.11 (SCL/SCLK), U2.2 (SCL)
SDA: CN1.9, U1.13 (SDA/MOSI), U2.1 (SDA)
VREF: R5.1, R6.2, U4.3 (+IN)

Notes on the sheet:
(I2C_ADDR: 0x03)
Released under the Creative Commons Attribution-ShareAlike 4.0 International (CC BY-SA 4.0)
http://creativecommons.org/licenses/by-sa/4.0/
Designed by: Peter Jansen
http://www.tricorderproject.org
Revision 0 (July 2014)
Arducorder Mini project
Lightning, UV, and Audio Front Sensor Board
CONNECTOR TO MOTHERBOARD
LIGHTNING SENSOR
UV SENSOR
AUDIO (MICROPHONE) SENSOR
NOTE: 100k/1.5k = 66X GAIN



Board: 2 copper layers, 30.0 x 15.0 mm, 22 parts (5 on the bottom side), 14 nets.

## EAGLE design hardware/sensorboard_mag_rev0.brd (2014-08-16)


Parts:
C3: 2.2nF 50V; 0603
C4, C5, C9: 0.1uF; 0603
C6: 10nF; 0603
C7: 4.7uF; 0603
C8: 0.22uF; 0603
CN1: CON-MOLEX-2MMMALE; MOLEX-0877591650
R5, R6: 4.7k; 0603
SJ1: SOLDERJUMPER_2WAYPASTE2&3; SJ_3_PASTE2&3
U$2: HMC5883LSMD; 16LPCC
U$10: MPU-9150; LGA-24-(4X4MM)

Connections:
3.3V: C5.1, C6.1, C9.1, CN1.2, R5.2, R6.2, SJ1.1, U$2.2 (VDD), U$2.4 (S1), U$2.13 (VDDIO), U$10.3 (VDD1), U$10.8 (VLOGIC), U$10.13 (VDD2)
GND: C3.2, C4.2, C5.2, C6.2, C7.2, C9.2, CN1.1, SJ1.3, U$2.9 (GND), U$2.11 (GND), U$10.1 (CLKIN), U$10.11 (FSYNC), U$10.15 (GND1), U$10.17 (GND2), U$10.18 (GND3)
HMC5883L_DRDY: CN1.10, U$2.15 (DRDY)
MPU9150_INT: CN1.14, U$10.12 (INT)
unnamed: SJ1.2, U$10.9 (AD0)
unnamed: C7.1, U$2.10 (C1)
unnamed: C3.1, U$10.20 (CPOUT)
unnamed: C4.1, U$10.10 (REGOUT)
unnamed: C8.1, U$2.12 (SETC)
unnamed: C8.2, U$2.8 (SETP)
SCL: CN1.11, R6.1, U$2.1 (SCL), U$10.23 (SCL)
SDA: CN1.9, R5.1, U$2.16 (SDA), U$10.24 (SDA)

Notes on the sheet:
(I2C_ADDRESS: 0x68)
(I2C_ADDR: 0x1E)
Released under the Creative Commons Attribution-ShareAlike 4.0 International (CC BY-SA 4.0)
http://creativecommons.org/licenses/by-sa/4.0/
Designed by: Peter Jansen
http://www.tricorderproject.org
Revision 0 (July 2014)
Arducorder Mini project
Magnetometer and IMU Sensor Board
INERTIAL MEASUREMENT UNIT
MAGNETOMETER
OPTIONAL
CONNECTOR TO MOTHERBOARD



Board: 2 copper layers, 14.0 x 19.0 mm, 13 parts (3 on the bottom side), 12 nets.

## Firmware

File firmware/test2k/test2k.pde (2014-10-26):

// main.c
// This firmware is a work in progress, and is currently test/development firmware 
// used to verify the functionality of the hardware.  

#include <Client.h>
#include <SPI.h>
#include <Wire.h>
#include <SD.h>
#include <math.h>
#include <I2Cdev.h>
#include <MPU6050.h>

// Graphics
#include "SSD1351.h"
#include "FramebufferGFX.h"
#include "FramebufferGraphs.h"

// Sensors
#include "Adafruit_MPR121.h"
#include "sensorbuffer.h"
#include "sensor_HMC5883L.h"
#include "sensor_microphone.h"
#include "Adafruit_SI1145.h"
#include "sensor_HTU21D.h"
#include "sensor_BMP180.h"
#include "sensor_AS3935.h"
#include "SensorMLX90620.h"
#include "SensorSpecHamamatsu.h"
#include "SensorRadiation.h"

// User Interface
#include "Tile.h"
#include "Fonts.h"
#include "Bitmaps.h"
#include "TileGUI.h"

// Communications
#include <Adafruit_CC3000.h>
#include "PlotlyInterface.h"


// Defines
#define SD_CS  84

#define TOUCH_HIST_SIZE  50

// Variables
SSD1351 Framebuffer;                        // Display driver
FramebufferGFX GFX(&Framebuffer);           // Graphics functions
FramebufferGraphs Graph(&GFX);              // Graph display/visualization
TileGUI tileGUI(&GFX);                      // Tile-based GUI

SensorBuffer sb(100);                       // Sensor buffer test
SensorBuffer sbx(100);                       // Sensor buffer test
SensorBuffer sby(100);                       // Sensor buffer test
SensorBuffer sbz(100);                       // Sensor buffer test
SensorBuffer sbMic(100);                       // Sensor buffer test
SensorBuffer sbTemp(100);                       // Sensor buffer test
SensorBuffer sbHumidity(100);                       // Sensor buffer test
SensorBuffer sbPressure(100);                       // Sensor buffer test
SensorBuffer sbAccelX(100);                       // Sensor buffer test
SensorBuffer sbAccelY(100);                       // Sensor buffer test
SensorBuffer sbAccelZ(100);                       // Sensor buffer test
SensorBuffer sbGyroX(100);                       // Sensor buffer test
SensorBuffer sbGyroY(100);                       // Sensor buffer test
SensorBuffer sbGyroZ(100);                       // Sensor buffer test
SensorBuffer sbRad(100);
SensorBuffer sbRadPWM(100);

SensorBuffer sbSpectBaseline(100);            // Sensor buffer test
SensorBuffer sbSpectMeasurement(100);            // Sensor buffer test
FramebufferGraphs SpectrometerGraph(&GFX);  
FramebufferGraphs SpectrometerBaselineGraph(&GFX);  
FramebufferGraphs RadiationPWMGraph(&GFX);  

// Sensor Variables
SensorHMC5883L sensorHMC5883L;                      // Magnetometer
Adafruit_MPR121 touchWheel = Adafruit_MPR121();     // MPR121 touch sensor
Adafruit_SI1145 uv = Adafruit_SI1145();             // SI1445 UV sensor
SensorMicrophone sensorMicrophone;                  // ADMP401 microphone
HTU21D sensorHTU21D;                                // HTU21D temperature/humidity sensor

Adafruit_BMP085_Unified bmp = Adafruit_BMP085_Unified(10085);  // BMP180 barometric pressure sensor

MPU6050 accelgyro(0x69); // <-- use for AD0 low     // MPU9150 Inertial measurement unit

SensorMLX90620 thermalImager;                       // MLX90620 16x4 Thermal Imager
SensorSpecHamamatsu sensorSpectrometer;             // Hamamatsu C12666MA micro spectroemter
SensorRadiation sensorRadiation(&sbRad);            // Radiation Watch Type 5 High-energy Particle Detector


// Plotly Web Interface
Adafruit_CC3000 cc3000(ADAFRUIT_CC3000_CS, ADAFRUIT_CC3000_IRQ, ADAFRUIT_CC3000_VBAT, SPI_CLOCK_DIV2);  
PlotlyInterface plotly = PlotlyInterface(&cc3000);
int plotlyLastUpdateSec = 0;
int plotlyFilenameIncrement = 1;      // Incrementing index appended to plotly saves

// User interface -- modes
uint8_t userInterfaceMode;
#define UI_MODE_TILE     10
#define UI_MODE_GRAPH    20

// User interface -- graph based displays
#define GRAPH_MAGXYZ         1
#define GRAPH_MAGSTRENGTH    2
#define GRAPH_MIC            3
#define GRAPH_HUMIDITY       4
#define GRAPH_PRESSURE       5
#define GRAPH_ACCELGYRO      6
#define GRAPH_RADIATION      7
#define GRAPH_SPECTROMETER   8
#define GRAPH_THERMAL        9
#define GRAPH_RADIATIONPWM   10

uint16_t showGraph = GRAPH_MAGXYZ;

// User interface -- push buttons (MPR121 electrode numbers)
#define BUTTON_TOUCH_SELECT    10  
#define BUTTON_TOUCH_BACK      9

// Temporary buffer for string operations
char stringBuffer[10];

// Functions
void setup() {
  Serial.begin(9600);
  Serial.println("Initializing... "); 

  // Initialize framebuffer
  Serial.println("Initializing Framebuffer...");  
  Framebuffer.begin();  
  GFX.displayFlashBitmap4Bit(5, 32, &symbArducorderSplashBitmap, 0);
  GFX.updateScreen();

  // Initialize touch
  Serial.println("Initializing MPR121...");  
  if (!touchWheel.begin(0x5A)) {
    Serial.println("MPR121 not found, check wiring?");
  }
  Serial.println("MPR121 found!");
  touchWheel.initTouchWheel(8, -20);
  touchWheel.takeWheelBaseline();  
  
  Serial.print("Initializing SD card...");
  pinMode(SD_CS, OUTPUT);
  digitalWrite(SD_CS, 1);
 
  // Disable CC3000 enable line
  pinMode(ADAFRUIT_CC3000_VBAT, OUTPUT);
  digitalWrite(ADAFRUIT_CC3000_VBAT, 0);
 
  // see if the card is present and can be initialized:
  // Note: I'm not sure why, but SD.begin() is failing, but subsequent functions seem fine. 
  if (!SD.begin(SD_CS)) {
    Serial.println("SD Card failed, or not present");
    Serial.println("Halting... ");
//    while(1);
    // don't do anything more:
//    return;
  }
  Serial.println("card initialized.");

  // Initialize sensors
  Serial.println("Initializing sensors...");
  Wire.begin();
  delay(500);

  // Initialize MLX90620
  Serial.println ("Initializing MLX90620...");
  thermalImager.begin();    
//  thermalImager.debugPrint();  
  
  // Initialize C12666MA Micro Spectrometer
  Serial.println ("Initializing C12666MA...");
  sensorSpectrometer.begin();    
  
  // Initialize HMC5883L
  Serial.println("Initializing HMC5883L...");
  sensorHMC5883L.init_HMC5883L();
  delay(500);
  
  // Initialize UV sensor
  Serial.println("Initializing UV Sensor...");
  uv.begin();
  
  // Initialize pressure sensor
  Serial.println("Initializing BMP180...");     
  if (!bmp.begin()) {
    Serial.println("ERROR: Could not initialize BMP180...");     
  }
  
  // Initialize AS3935 
  //Serial.println("Initializing AS3935...");     
  //AS3935_setup();
   
  // Initialize MPU6050
  Serial.println("Initializing MPU9050...");     
  accelgyro.initialize();
  Serial.println(accelgyro.testConnection() ? "MPU6050 connection successful" : "MPU6050 connection failed");   

    
  // Initialize Radiation sensor (interrupt driven)
  Serial.println("Initializing Radiation sensor...");       
  setupRadiationISR(&sensorRadiation);     // MUST be called before begin()
  sensorRadiation.begin();


  // Re-initialize the MLX90620 
  // TODO: The thermal imager seems to require initialization twice -- check into this
  Serial.println("Initializing Thermal Imager...");  
  thermalImager.begin();    

  // Visualization
  Serial.println("Initializing Sensor Graph...");  
  initSensorGraph();
  
  
  
  // ******************************************
  // Initialize Tile-based GUI
  // ******************************************  
  Serial.println ("Initializing tileGUI");

     
  // ******************************************     
  // Initialize tiles 
  // ******************************************
  // THEME: Ambient atmospheric measurements
  // ******************************************  
  // TILE: Ambient Temperature (1x1)
  Serial.println ("Adding tile...");
  tileGUI.addTile(TILE_ATMTEMP)->Initialize("Temp", RGB(0, 0, 128), &symbTempBitmap, &sbTemp);
  // Set unit text to "[degree]C"
  strcpy(stringBuffer, " C");
  stringBuffer[0] = 176;
  tileGUI.getTile(TILE_ATMTEMP)->setUnitText(stringBuffer);
  
  // TILE: Ambient Humidity (1x1)
  Serial.println ("Adding tile...");
  tileGUI.addTile(TILE_ATMHUMIDITY)->Initialize("Humidity", RGB(0, 0, 128), &symbHumidityBitmap, &sbHumidity);
  tileGUI.getTile(TILE_ATMHUMIDITY)->setUnitText("%");
  
  // TILE: Ambient Pressure (2x1)
  Serial.println ("Adding tile...");
  tileGUI.addTile(TILE_ATMPRESSURE)->Initialize("Pressure", RGB(0, 128, 0), &symbPressureBitmap, &sbPressure);
  tileGUI.getTile(TILE_ATMPRESSURE)->setSize(2, 1);
  tileGUI.getTile(TILE_ATMPRESSURE)->setUnitText("mbar");    
  tileGUI.getTile(TILE_ATMPRESSURE)->setSensorTextFormat(TEXT_FLOAT1DEC);
  
  // ******************************************  
  // THEME: Electromagnetic Readings (1)
  // ******************************************  
  // TILE: Magnetic Field Strength (1x1)
  Serial.println ("Adding tile...");
  tileGUI.addTile(TILE_MAGFIELD)->Initialize("Magnetic", RGB(0, 0, 128), &symbMagBitmap, &sb);
  strcpy(stringBuffer, " T");
  stringBuffer[0] = 181;
  tileGUI.getTile(TILE_MAGFIELD)->setUnitText(stringBuffer);
  
  // TILE: Magnetic Field Direction (1x1)  
  // NOTE: Arrow tile currently unimplemented
  Serial.println ("Adding tile...");
  tileGUI.addTile(TILE_MAGDIR)->Initialize("Magnetic", RGB(0, 0, 128), &symbMagBitmap, NULL);
  tileGUI.getTile(TILE_MAGDIR)->setText("DIR");

  // TILE: Lightning (strike distance) (1x1)
  Serial.println ("Adding tile...");
  tileGUI.addTile(TILE_LIGHTNING_STR)->Initialize("Lightning", RGB(0, 0, 128), &symbLightningBitmap, NULL);
  tileGUI.getTile(TILE_LIGHTNING_STR)->setText("5");
  tileGUI.getTile(TILE_LIGHTNING_STR)->setUnitText("km");

  // TILE: Radiation (counts per minute) (1x1)
  Serial.println ("Adding tile...");
  tileGUI.addTile(TILE_RADIATION_CPM)->Initialize("Radiation", RGB(0, 0, 128), &symbRadiationBitmap, NULL);
  tileGUI.getTile(TILE_RADIATION_CPM)->setUnitText("cpm");



  // ******************************************
  // THEME: Electromagnetic Readings (2)
  // ******************************************  
  // TILE: Spectrometer (2x1)
  // NOTE: Spectrum (1D data) tile
  Serial.println ("Adding tile...");
  tileGUI.addTile(TILE_SPECTROMETER)->Initialize("Spectrum", RGB(0, 0, 128), NULL, NULL);
  tileGUI.getTile(TILE_SPECTROMETER)->setSize(2, 1);
  tileGUI.getTile(TILE_SPECTROMETER)->setText("");   
  
  SpectrometerGraph.clearSeries();
  SpectrometerGraph.addSeries( &sbSpectMeasurement, RGB(128, 128, 255) );
  tileGUI.getTile(TILE_SPECTROMETER)->setLiveGraph(&SpectrometerGraph);   

  
  // TILE: UV (1x1)
  Serial.println ("Adding tile...");
  tileGUI.addTile(TILE_UV)->Initialize("UV Index", RGB(128, 0, 128), &symbUVBitmap, NULL);
  tileGUI.getTile(TILE_UV)->setText("0");  
  tileGUI.getTile(TILE_UV)->setUnitText("i");

  // TILE: Linear Polarization (1x1)  
  Serial.println ("Adding tile...");  
  tileGUI.addTile(TILE_LINEAR_POL)->Initialize("Polarization", RGB(128, 0, 128), &symbPolarizationBitmap, NULL);
  tileGUI.getTile(TILE_LINEAR_POL)->setText("25");
  tileGUI.getTile(TILE_LINEAR_POL)->setUnitText("%");  

  
        
        
  // ******************************************        
  // THEME: Electromagnetic Readings (3)
  // ******************************************  
  // TILE: Thermal Imager (16x4)
  // NOTE: Image (2D data) tile
  Serial.println ("Adding tile...");
  tileGUI.addTile(TILE_THERMAL_CAM)->Initialize("Thermal", RGB(0, 0, 128), NULL, NULL);
  tileGUI.getTile(TILE_THERMAL_CAM)->setSize(1, 2);
  tileGUI.getTile(TILE_THERMAL_CAM)->setText("");   
  tileGUI.getTile(TILE_THERMAL_CAM)->setLiveBitmap(&thermalImager.image[0][0], 4, 16);
  
  // TILE: Lightning (disturber) (1x1)
  Serial.println ("Adding tile...");  
  tileGUI.addTile(TILE_LIGHTNING_DIS)->Initialize("Disturber", RGB(0, 0, 128), &symbLightningBitmap, NULL);
  tileGUI.getTile(TILE_LIGHTNING_DIS)->setText("1");  
  tileGUI.getTile(TILE_LIGHTNING_DIS)->setUnitText("km");
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

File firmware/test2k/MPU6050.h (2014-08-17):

// I2Cdev library collection - MPU6050 I2C device class
// Based on InvenSense MPU-6050 register map document rev. 2.0, 5/19/2011 (RM-MPU-6000A-00)
// 10/3/2011 by Jeff Rowberg <jeff@rowberg.net>
// Updates should (hopefully) always be available at https://github.com/jrowberg/i2cdevlib
//
// Changelog:
//     ... - ongoing debug release

// NOTE: THIS IS ONLY A PARIAL RELEASE. THIS DEVICE CLASS IS CURRENTLY UNDERGOING ACTIVE
// DEVELOPMENT AND IS STILL MISSING SOME IMPORTANT FEATURES. PLEASE KEEP THIS IN MIND IF
// YOU DECIDE TO USE THIS PARTICULAR CODE FOR ANYTHING.

/* ============================================
I2Cdev device library code is placed under the MIT license
Copyright (c) 2012 Jeff Rowberg

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
THE SOFTWARE IS PROVIDED "AS IS", WITHOUT WARRANTY OF ANY KIND, EXPRESS OR
IMPLIED, INCLUDING BUT NOT LIMITED TO THE WARRANTIES OF MERCHANTABILITY,
FITNESS FOR A PARTICULAR PURPOSE AND NONINFRINGEMENT. IN NO EVENT SHALL THE
AUTHORS OR COPYRIGHT HOLDERS BE LIABLE FOR ANY CLAIM, DAMAGES OR OTHER
LIABILITY, WHETHER IN AN ACTION OF CONTRACT, TORT OR OTHERWISE, ARISING FROM,
OUT OF OR IN CONNECTION WITH THE SOFTWARE OR THE USE OR OTHER DEALINGS IN
THE SOFTWARE.
===============================================
*/

#ifndef _MPU6050_H_
#define _MPU6050_H_

#include "I2Cdev.h"

// supporting link:  http://forum.arduino.cc/index.php?&topic=143444.msg1079517#msg1079517
// also: http://forum.arduino.cc/index.php?&topic=141571.msg1062899#msg1062899s
//#ifndef __arm__
//#include <avr/pgmspace.h>
//#else
#define PROGMEM /* empty */
#define pgm_read_byte(x) (*(x))
#define pgm_read_word(x) (*(x))
#define pgm_read_float(x) (*(x))
#define PSTR(STR) STR
//#endif


#define MPU6050_ADDRESS_AD0_LOW     0x68 // address pin low (GND), default for InvenSense evaluation board
#define MPU6050_ADDRESS_AD0_HIGH    0x69 // address pin high (VCC)
#define MPU6050_DEFAULT_ADDRESS     MPU6050_ADDRESS_AD0_LOW
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

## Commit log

2014-08-16 Added initial hardware source files
    [motherboard_rev0.brd, motherboard_rev0.sch, sensorboard_atm_rev0.brd, sensorboard_atm_rev0.sch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]
2014-08-17 Added test firmware in it's current state
2014-08-26 Added revision 1 of the atmospheric sensor board, with MOSFETs for the MiCS6814 gas sensor
    [sensorboard_atm_rev1.brd, sensorboard_atm_rev1.sch]
2014-08-26 minor changes
    [motherboard_rev1.brd, motherboard_rev1.sch]
2014-09-01 Added spectrometer and thermal camera board (rev0)
    [sensorboard_spectrometer_rev0.brd, sensorboard_spectrometer_rev0.sch]
2014-09-04 Added spectrometer sensor board gerbers
2014-09-07 added gradientRect() to Framebuffer Graphics Library
2014-09-12 Added prototype automated tile packer for TileGUI
2014-09-19 Minor change -- SensorBuffer now has a function to return the most recently stored value, and the Tile constructor now accepts a SensorBuffer pointer that it can draw data from
2014-09-25 Added Hue (HSB) to RGB converter, and temperature-based color map
2014-09-26 Fixed issues with spectrometer tile -- SensorBuffer is statically sized, so had to resample spectrometer data to buffer size in populateSensorBuffer(). Result is too cool!
2014-09-27 Updated MPR121 library to detect pushbuttons. Currently detects buttons using capacitance instead of the GPIO library
2014-10-07 Added revision 1 to motherboard, as well as CHANGELOG file
    [motherboard_rev1.brd, motherboard_rev1.sch]
2014-10-07 Added capacitive touch board, revision 2, which moves most of the parts to the bottom of the board, adds mounting holes, and matches the motherboard rev1 footprint
    [touch_rev2.brd, touch_rev2.sch]
2014-10-08 Added motherboard rev1 and capacitive touch board rev2
    [motherboard_rev1.brd, motherboard_rev1.sch, touch_rev2.brd, touch_rev2.sch]
2014-10-09 Added radiation sensor board rev1
    [sensorboard_radiation_rev1.brd, sensorboard_radiation_rev1.sch]
2014-10-23 Change to capacitive touch wheel calibration for acrylic faceplate. Minor bugfix for thermal display tile
2014-10-23 Code for Si1145 UV sensor enabled and working
2014-10-24 Minor revisions to motheboard (moved SD card over 2mm)
    [motherboard_rev1a.brd, motherboard_rev1a.sch]
2014-10-28 Added laser cut patterns for case
2014-10-28 Added CC3000 driver patch example from Adafruit, with pin configurations for Arducorder Mini
2014-10-28 Added lightning sensor board gerbers
2014-11-10 Changed partslists from txt to XLS format. Added formatting and source information for trickier parts
    [motherboard_rev1_partslist.xls, sensorboard_atm_rev1_partslist.xls, sensorboard_lightning_rev0_partslist.xls, sensorboard_mag_rev0_partslist.xls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]
2014-11-10 minor cleanup
    [sensorboard_lightning_rev0_partslist.xls]

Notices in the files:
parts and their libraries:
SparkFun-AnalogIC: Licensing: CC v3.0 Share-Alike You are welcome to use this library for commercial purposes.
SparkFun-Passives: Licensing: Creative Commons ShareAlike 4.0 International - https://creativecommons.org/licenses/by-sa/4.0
